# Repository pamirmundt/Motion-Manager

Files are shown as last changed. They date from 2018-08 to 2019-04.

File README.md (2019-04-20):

# Motion Manager (v1.0.0)
Controller for HNP Mikrosysteme micro annular gear pump MZR-7223
- 100 Hz PI RPM control with a RPM MAP filter
- 5 Hz screen refresh
- 31.250 Hz PWM frequency

## Future Improvements
- Spaghetti code
- SD card reader and LCD need different SPI busses. (because LCD SPI does not have a CS option where SPI messes)
- 24V converter for fixed input
- Converter efficiency and heat problems with linear regulators (Linear regulator must be replaced with a switching converter)
- Voltage protection
- SPI is not enough for LCD, additional data bus lines should be used for feedback from LCD

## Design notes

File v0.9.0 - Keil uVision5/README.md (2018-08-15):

# MotionManager v0.9.0

- [X] Keil uVision5 project files
- [X] RPM Control
- [X] Voltage Control

- [ ] SD card support
- [ ] Logo reveal
- [ ] Flow rate display

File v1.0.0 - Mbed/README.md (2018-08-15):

# MotionManager v1.0.0

- [X] Mbed project files
- [X] RPM Control
- [X] Voltage Control
- [X] SD card support
- [X] Logo reveal
- [X] Flow rate display

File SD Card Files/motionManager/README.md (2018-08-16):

# About
#### SD card provides configuration parameters to MotionManager.
#### MotionManager only reads SD card on boot, during logo reveal.
#### MotionManager should be turned off and on, if any changes are done on the SD card.
#### SD card folder hierarchy should be "SDcard:\motionManager\configFile.csv"
#### If no SD card is provided or there is a missing .csv file, MotionManager uses its build in default parameters.
#### All parameters are in floating points and the syntax is "10.0,20.0,30.0", with commas between parameters and without any spaces.

## PID.csv

### (Kp,Ki,Kd,integralMin,integralMax,alpha)
#### Kp: Proportional Coefficient
#### Ki: Integral Coefficient
#### Kd: Derivative Coefficient
#### integralMin: Integral Sum Minimum Threshold
#### integralMax: Integral Sum Maximum Threshold
#### alpha: Moving average filter alpha value, [ accumulator = (alpha * new_value) + (1.0 - alpha) * accumulator ]

##### More about PID: https://en.wikipedia.org/wiki/PID_controller
##### More about moving average filter: https://en.wikipedia.org/wiki/Moving_average

## RPM.csv

### (refRpmResolution, refRpmUpperThreshold)
#### refRpmResolution: Reference RPM Resolution
#### refRpmUpperThreshold: Maximum Selectable Reference RPM

## encoder.csv

### (encoderPulsePerRev)
#### encoderPulsePerRev: Encoder Resolution / Pulses Per Revolution

##### More about encoders: https://en.wikipedia.org/wiki/Rotary_encoder

## flowRateVersusVoltage.csv

### (A,B,C)
#### Quadratic function constants for Flow Rate(ml/min) versus voltage
#### Flow Rate = A * (Voltage)^2 + B * voltage + C

##### Quadratic curve fitting: https://www.wolframalpha.com/input/?i=quadratic+fit&lk=3

## voltage.csv

### (voltageResolution,voltageUpperThreshold)
#### voltageResolution: Selectable voltage resolution
#### voltageUpperThreshold: Maximum selectable voltage

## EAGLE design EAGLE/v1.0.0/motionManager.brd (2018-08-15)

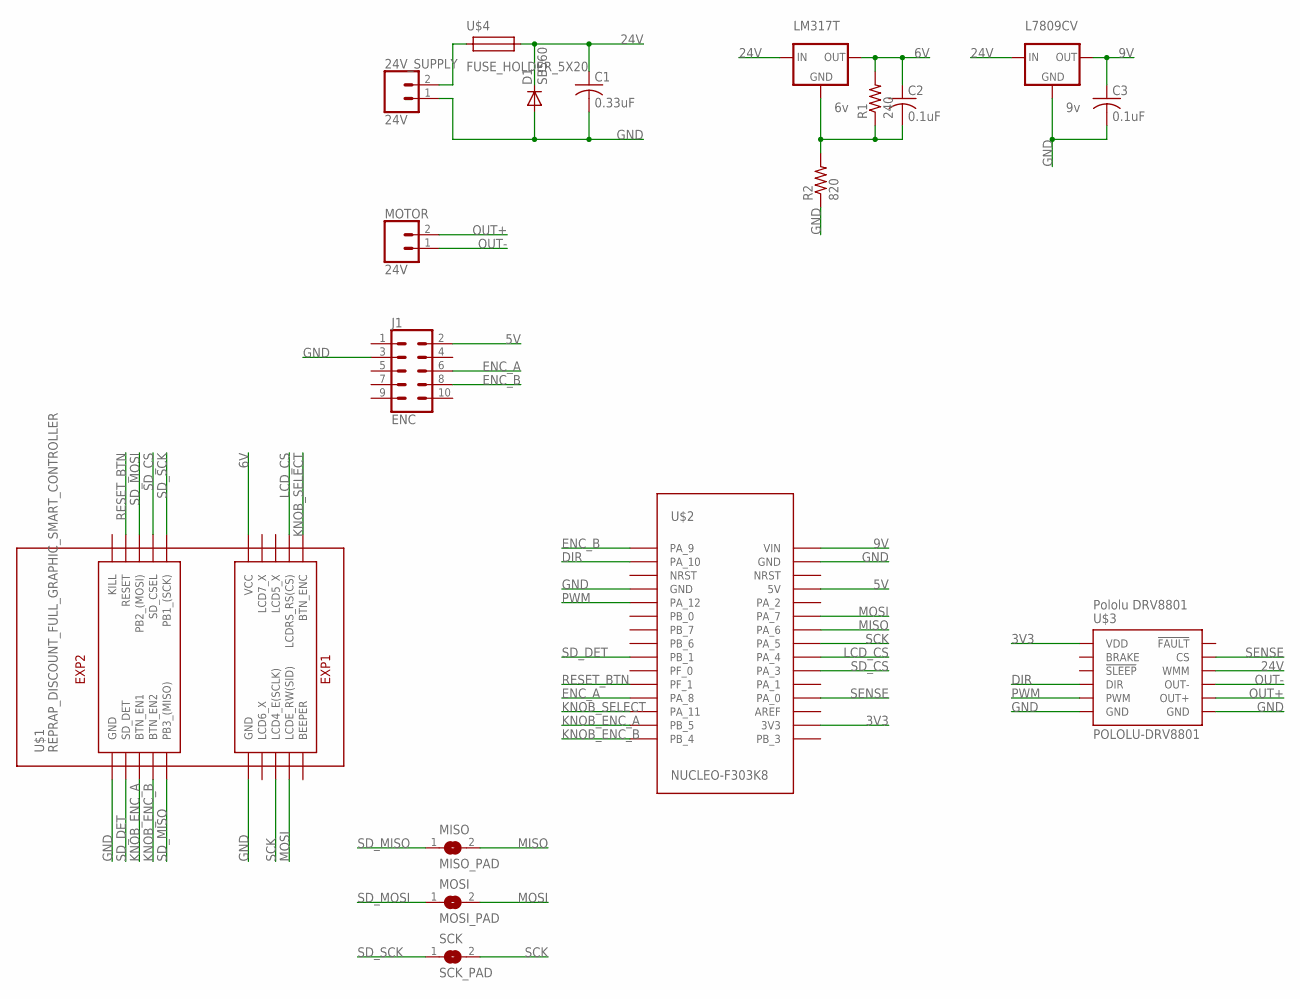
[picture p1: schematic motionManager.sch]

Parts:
24V_SUPPLY: 24V; SCREWTERMINAL-5MM-2
C1: 0.33uF; C025_050-055X075
C2, C3: 0.1uF; C025_050-055X075
D1: SB560; DO201-15
J1: ENC; 2X5-SHROUDED-NS
L7809CV: 9v; 78XXL
LM317T: 6v; 78XXL
MISO: MISO_PAD; SJW
MOSI: MOSI_PAD; SJW
MOTOR: 24V; SCREWTERMINAL-5MM-2
R1: 240; 0207/7
R2: 820; 0207/7
SCK: SCK_PAD; SJW
U$1: REPRAP_DISCOUNT_FULL_GRAPHIC_SMART_CONTROLLER
U$2: NUCLEO-F303K8
U$3: POLOLU-DRV8801
U$4: FUSE_HOLDER_5X20

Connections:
3V3: U$2.3V3, U$3.VDD
5V: J1.2, U$2.5V
6V: C2.1, LM317T.OUT, R1.2, U$1.VCC
9V: C3.1, L7809CV.OUT, U$2.VIN
24V: C1.1, D1.C, L7809CV.IN, LM317T.IN, U$3.VMM (WMM), U$4.P$2
DIR: U$2.PA_10, U$3.DIR
ENC_A: J1.6, U$2.PA_8
ENC_B: J1.8, U$2.PA_9
GND: 24V_SUPPLY.1, C1.2, C3.2, D1.A, J1.3, L7809CV.GND, R2.1, U$1.GND@0 (GND), U$1.GND@1 (GND), U$2.GND@0 (GND), U$2.GND@1 (GND), U$3.GND@1 (GND), U$3.GND@2 (GND)
KNOB_ENC_A: U$1.BTN_EN1, U$2.PB_5
KNOB_ENC_B: U$1.BTN_EN2, U$2.PB_4
KNOB_SELECT: U$1.BTN_ENC, U$2.PA_11
LCD_CS: U$1.LCDRS_RS(CS), U$2.PA_4
MISO: MISO.2, U$2.PA_6
MOSI: MOSI.2, U$1.LCDE_RW(SID), U$2.PA_7
unnamed: 24V_SUPPLY.2, U$4.P$1
unnamed: C2.2, LM317T.GND, R1.1, R2.2
OUT+: MOTOR.2, U$3.OUT+
OUT-: MOTOR.1, U$3.OUT-
PWM: U$2.PA_12, U$3.PWM
RESET_BTN: U$1.RESET, U$2.PF_1
SCK: SCK.2, U$1.LCD4_E(SCLK), U$2.PA_5
SD_CS: U$1.SD_CSEL, U$2.PA_3
SD_DET: U$1.SD_DET, U$2.PB_1
SD_MISO: MISO.1, U$1.PB3_(MISO)
SD_MOSI: MOSI.1, U$1.PB2_(MOSI)
SD_SCK: SCK.1, U$1.PB1_(SCK)
SENSE: U$2.PA_0, U$3.CS

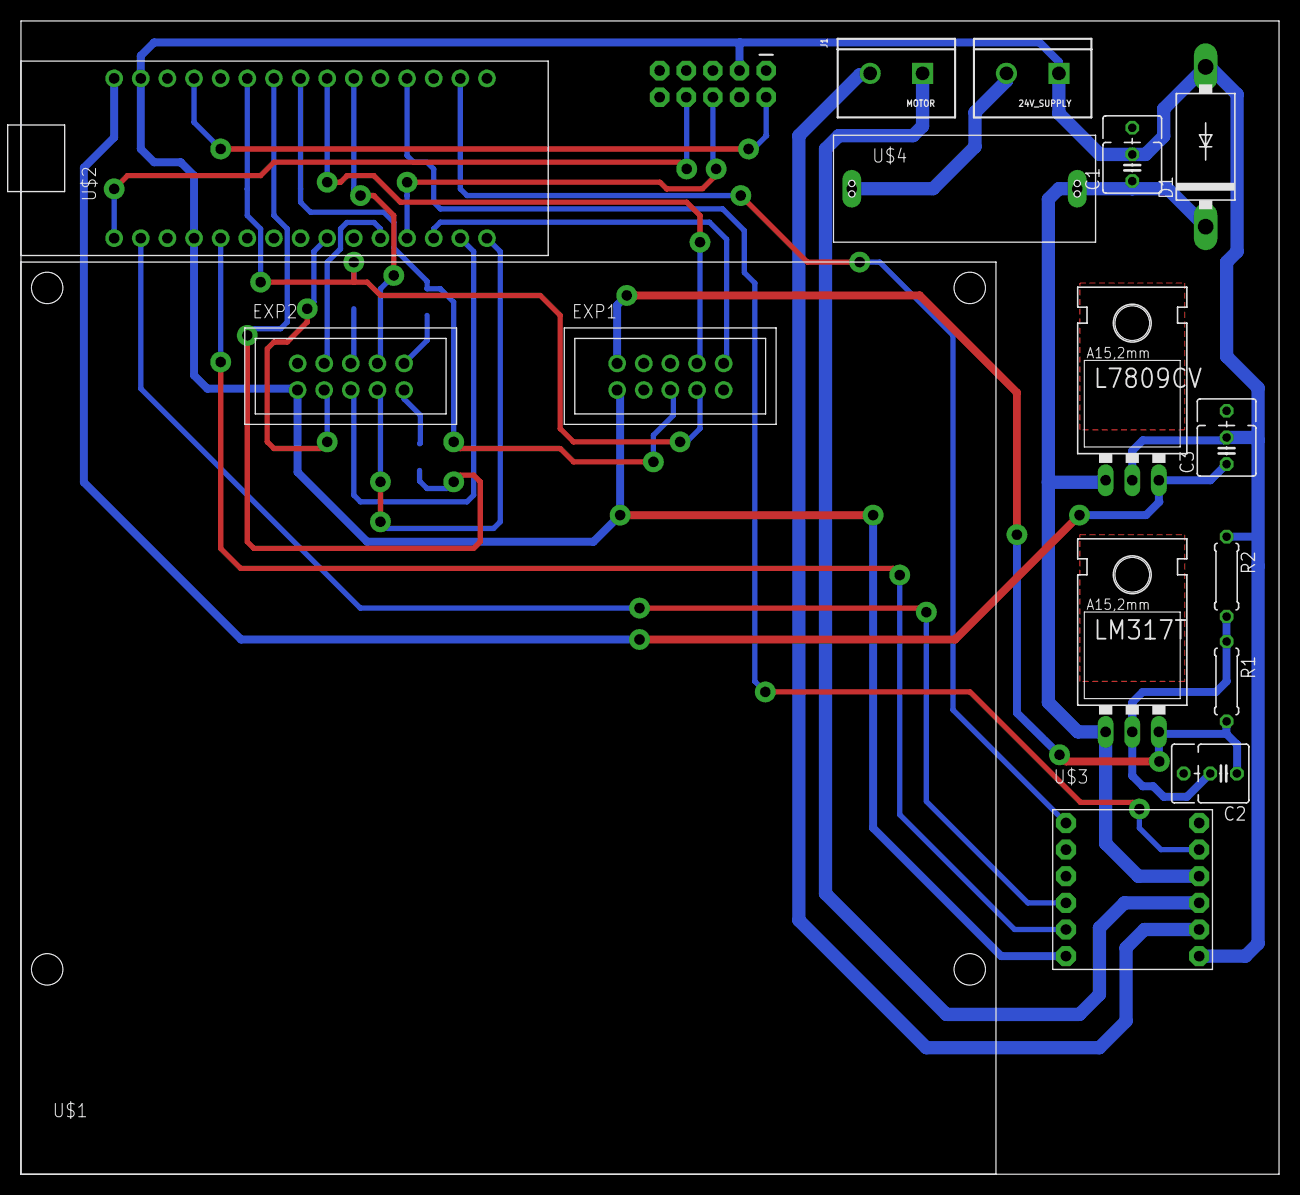
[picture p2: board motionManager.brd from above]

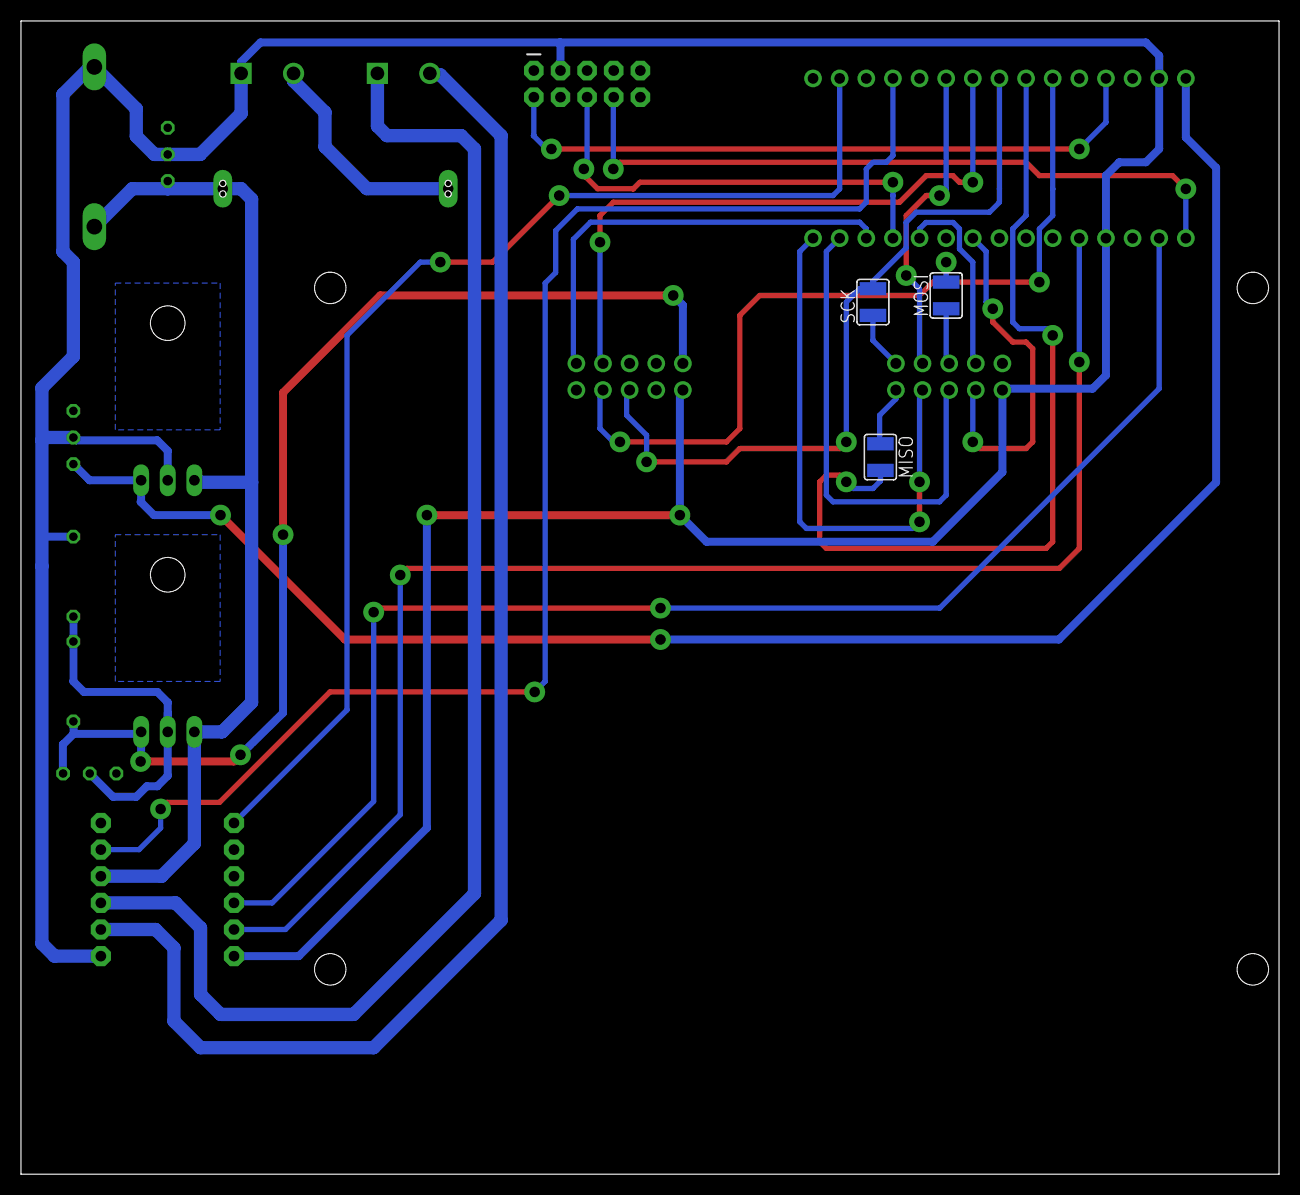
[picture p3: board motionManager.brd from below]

Board: 2 copper layers, 120.0 x 110.0 mm, 18 parts (3 on the bottom side), 28 nets.

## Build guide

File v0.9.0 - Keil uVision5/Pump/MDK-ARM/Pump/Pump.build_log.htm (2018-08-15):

µVision Build Log

Tool Versions:

IDE-Version: µVision V5.24.2.0
Copyright (C) 2017 ARM Ltd and ARM Germany GmbH. All rights reserved.
License Information: Pamir Mundt, Sabanci University, LIC=----
 
Tool Versions:
Toolchain:       MDK-Lite  Version: 5.24.1
Toolchain Path:  D:\Keil_v5\ARM\ARMCC\Bin
C Compiler:      Armcc.exe V5.06 update 5 (build 528)
Assembler:       Armasm.exe V5.06 update 5 (build 528)
Linker/Locator:  ArmLink.exe V5.06 update 5 (build 528)
Library Manager: ArmAr.exe V5.06 update 5 (build 528)
Hex Converter:   FromElf.exe V5.06 update 5 (build 528)
CPU DLL:         SARMCM3.DLL V5.24.1
Dialog DLL:      DCM.DLL V1.16.0.0
Target DLL:      STLink\ST-LINKIII-KEIL_SWO.dll V3.0.1.0
Dialog DLL:      TCM.DLL V1.32.0.0

Project:

C:\Users\Mundt\Desktop\Pump\MDK-ARM\Pump.uvprojx
Project File Date:  08/09/2018

Output:

*** Using Compiler 'V5.06 update 5 (build 528)', folder: 'D:\Keil_v5\ARM\ARMCC\Bin'
Build target 'Pump'
"Pump\Pump.axf" - 0 Error(s), 0 Warning(s).

Software Packages used:

Package Vendor: ARM
                http://www.keil.com/pack/ARM.CMSIS.5.3.0.pack
                ARM.CMSIS.5.3.0
                CMSIS (Cortex Microcontroller Software Interface Standard)
   * Component: CORE Version: 5.1.1

Package Vendor: Keil
                http://www.keil.com/pack/Keil.STM32F3xx_DFP.2.1.0.pack
                Keil.STM32F3xx_DFP.2.1.0
                STMicroelectronics STM32F3 Series Device Support and Examples

Collection of Component include folders:

  .\RTE\_Pump
  D:\Keil_v5\ARM\PACK\ARM\CMSIS\5.3.0\CMSIS\Include
  D:\Keil_v5\ARM\PACK\Keil\STM32F3xx_DFP\2.1.0\Drivers\CMSIS\Device\ST\STM32F3xx\Include

Collection of Component Files used:

   * Component: ARM::CMSIS:CORE:5.1.1
Build Time Elapsed:  00:00:01

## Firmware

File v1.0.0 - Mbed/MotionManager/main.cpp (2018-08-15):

#include "mbed.h"
#include "main.h"
#include "LCD.h"
#include "SDFileSystem.h"
#include "logo.h"

// DEBUG
//Serial pc(SERIAL_TX, SERIAL_RX);

/* Private variables ---------------------------------------------------------*/
SPI_HandleTypeDef hspi1;
TIM_HandleTypeDef htim1;
TIM_HandleTypeDef htim3;
TIM_HandleTypeDef htim15;
TIM_HandleTypeDef htim16;
TIM_HandleTypeDef htim17;

// mosi, miso, sclk, cs
SDFileSystem sd(PA_7, PA_6, PA_5, PA_3, "sd");

/* Private variables ---------------------------------------------------------*/
#define encodingType 4.0f //Quadrature Encoding
#define RPMCalculationFreq 100.0f

#define pwmResolution 2048

#define debounceMillis 400

LCD * lcd;

/*******************************************************************************
    RPM Resolution per encoder tick
        (Encoder tick/sec) to RPM

                        60sec * (Frequency of RPM calculation timer)
    RPM_res_per_tick = ----------------------------------------------
                        Encoder Resolution * Encoder Reading Mode(x4)
*******************************************************************************/
#define RPM_res_per_tick (60.0f * RPMCalculationFreq) / (encoderPulsePerRev * encodingType)

// RPM Calculation
volatile int16_t prevEncoderCount = 0;
volatile float motorRPM = 0.0f;

//Moving Average for RPM smoothing
volatile float averagedMotorRpm = 0.0f;
volatile float alpha = 0.128f;

// Voltage Control
volatile float voltage = 0.0f;

// PI Control
volatile float Kp = 0.02f;
volatile float Ki = 0.01f;
volatile float Kd = 0.0f;
volatile float integral = 0.0f;
volatile float integralMin = -2048.0f;
volatile float integralMax = 2048.0f;

volatile float refRpm = 0.0f;

// Encoder
float encoderPulsePerRev = 100.0f;

// Voltage
float voltageLowerThreshold = 0.0f;
float voltageUpperThreshold = 24.0f;
float voltageResolution = 0.1f;

// RPM
float refRpmLowerThreshold = 0.0f;
float refRpmUpperThreshold = 10000.0f;
float refRpmResolution = 100.0f;

//Flow Rate
//volatile float flowRate = 0.0f;
// Flow Rate versus Voltage
// Quadratic Function Parameters
// FR = f(V) = A*V^2 + B*V + C
float A = 0.0f, B = 0.0f, C = 0.0f;

//Display Selection
volatile float displayedRefRpm = 0.0f;
volatile float displayedVoltage = 0.0f;

// Rotary Knob
volatile uint8_t prevState = 0;
volatile int16_t cycleCount = 0;

//Debouncing
uint32_t currentMillis = 0;
uint32_t prevMillis = 0;

int pwm = 0;

const int cw[4] = {
              2, // 10 -> 11
              0, // 00 -> 10
              3, // 11 -> 01
              1  // 01 -> 00
            };

const int ccw[4] = {
              1, // 01 -> 11
              3, // 11 -> 10
              0, // 00 -> 01
              2  // 10 -> 00
            };

            
// Screen Menu Button Track - Select and Deselect
uint8_t selected = false;

// Underline of "Ref RPM"
uint8_t underlineHighlighted = false;
            
// Menu
enum menu{
    Logo,
    ControlSelection,
    RpmControl,
    VoltageControl,
    About
};

/* Private function prototypes -----------------------------------------------*/
void SystemClock_Config(void);
static void MX_GPIO_Init(void);
static void MX_TIM1_Init(void);
static void MX_TIM16_Init(void);
static void MX_TIM3_Init(void);
static void MX_SPI1_Init(void);
static void MX_TIM17_Init(void);
static void MX_TIM15_Init(void);

void HAL_TIM_MspPostInit(TIM_HandleTypeDef *htim);

enum menu menuSelection = Logo;

void applyPWM(int16_t pwmValue){
    //Forward
    if(pwmValue > 0){
        if(pwmValue > pwmResolution){
            pwmValue = pwmResolution;
            pwm = pwmValue;
        }
        HAL_GPIO_WritePin(GPIOA, GPIO_PIN_10, GPIO_PIN_RESET);
    }
    //Backward
    else{
        if(pwmValue < -pwmResolution){
            pwmValue = -pwmResolution;
            pwm = pwmValue;
        }
        HAL_GPIO_WritePin(GPIOA, GPIO_PIN_10, GPIO_PIN_SET);
    }
    pwmValue = abs(pwmValue);
    pwm = pwmValue;
    __HAL_TIM_SET_COMPARE(&htim16, TIM_CHANNEL_1, pwmValue);
}

// Increase Displayed Reference RPM
void incrementDisplayedRefRPM(void){
    if(displayedRefRpm < refRpmUpperThreshold)
        displayedRefRpm += refRpmResolution;
}

// Decrease Displayed Reference RPM
void decreaseDisplayedRefRPM(void){
    if(refRpmLowerThreshold < displayedRefRpm)
        displayedRefRpm -= refRpmResolution;
}

// Increase Displayed Voltage
void incrementDisplayedVoltage(void){
    if(displayedVoltage < voltageUpperThreshold)
        displayedVoltage += voltageResolution;
}

// Decrease Displayed Voltage
void decreaseDisplayedVoltage(void){
    if(voltageLowerThreshold < displayedVoltage)
        displayedVoltage -= voltageResolution;
}

//Count the Digits before .
uint8_t digitsInFloat(unsigned char * f){
    uint8_t i = 0;
    uint8_t digitCount = 0;
    while(f[i++] != '.'){
        digitCount++;
    }
    return digitCount;
}

//Calculate Flow Rate from Voltage - Quadratic Function
float calculateFlowRate(float _volt){
    float flowRate = (A * _volt * _volt) + (B * _volt) + C;
    return flowRate;
}

//Refresh Numbers on the screen
void refreshScreen(void){
    //Clear Second Row - Fill with Spaces
    DisplayStringLeftAlligned(lcd,1,0, (unsigned char *)"                ", strlen("                "));
    //Clear Fourth Rows First Half - Fill with Spaces
    DisplayStringLeftAlligned(lcd,3,0, (unsigned char *)"        ", strlen("        "));

    unsigned char * array = (unsigned char *)malloc(16);
    
    if(menuSelection == RpmControl){
        if(selected == true)
            sprintf((char *)array, "%.1f", displayedRefRpm);
        else if(selected == false)
            sprintf((char *)array, "%.1f", refRpm);
    }
    else if(menuSelection == VoltageControl){
        if(selected == true){
            sprintf((char *)array, "%.1f", displayedVoltage);
        }
        else if(selected == false){
            sprintf((char *)array, "%.1f", voltage);
        }
    }
    
    uint8_t digitCount = digitsInFloat(array);

    // Display Reference RPM
    DisplayStringRightAlligned(lcd,1,6, array, digitsInFloat(array)+2);
    
    free(array);

    // RPM
    unsigned char * rpmStr = (unsigned char *)malloc(16); //16 digits max
    sprintf((char *)rpmStr, "%.1f", averagedMotorRpm);
    DisplayStringRightAlligned(lcd,1,15, rpmStr, digitsInFloat(rpmStr)+2);
    free(rpmStr);
    
    //Calculate Flow Rate
    float flowRate =0.0f;
    if(menuSelection == RpmControl)
        flowRate = calculateFlowRate(((float)pwm / ((float)pwmResolution)) * voltageUpperThreshold);
    else if(menuSelection == VoltageControl)
        flowRate = calculateFlowRate(voltage);
        
    // Flow Rate
    unsigned char * flowRateStr = (unsigned char *)malloc(16);
    sprintf((char *)flowRateStr, "%.1f", flowRate);
    DisplayStringRightAlligned(lcd,3,7, flowRateStr, digitsInFloat(flowRateStr)+2);
    free(flowRateStr);
}

// Display underline of Ref RPM
void underlineHighlight(void){
    WriteInstruction(lcd, SET_GRAPHIC_RAM_ADDRESS | 29);
    WriteInstruction(lcd, 0x80);
    WriteRam(lcd, 0x7F);
    WriteRam(lcd, 0xFF);
    WriteRam(lcd, 0xFF);
    WriteRam(lcd, 0xFF);
    WriteRam(lcd, 0xFF);
    WriteRam(lcd, 0xFF);
    WriteRam(lcd, 0xFF);
}

// Hide underline of Ref RPM
void underlineLowlight(void){
    WriteInstruction(lcd, SET_GRAPHIC_RAM_ADDRESS | 29);
    WriteInstruction(lcd, 0x80);
    WriteRam(lcd, 0x00);
    WriteRam(lcd, 0x00);
    WriteRam(lcd, 0x00);
    WriteRam(lcd, 0x00);
    WriteRam(lcd, 0x00);
    WriteRam(lcd, 0x00);
    WriteRam(lcd, 0x00);
}

// Display Logo

// Display ControlSelection
uint8_t menuIndex = 0;

void menuControlSelection(void){
    menuSelection = ControlSelection;
    
    SetTextMode(lcd);
    ClearScreen(lcd);
    
    SetGraphicsMode(lcd);
    ClearGDRAM(lcd);
    
    for(uint8_t y = 0; y < 15; y++){
        for (uint8_t x = 0; x < 8; x++) {
            WriteInstruction(lcd, SET_GRAPHIC_RAM_ADDRESS | y);
            WriteInstruction(lcd, 0x80 | x);
            WriteRam(lcd, 0xFF);
            WriteRam(lcd, 0xFF);
        }
    }
        
    menuIndex = 1;
    HighlightMenuItem(lcd,menuIndex,true);
        
    SetTextMode(lcd);
    //ClearScreen(lcd);
    
    DisplayStringLeftAlligned(lcd,0,1, (unsigned char *)"MOTION MANAGER", strlen("MOTION MANAGER"));
    DisplayStringLeftAlligned(lcd,1,1, (unsigned char *)"RPM Control", strlen("RPM Control"));
    DisplayStringLeftAlligned(lcd,2,1, (unsigned char *)"Voltage Control", strlen("Voltage Control"));
    DisplayStringLeftAlligned(lcd,3,1, (unsigned char *)"About", strlen("About"));
}

void menuRpmControl(void){
    SetTextMode(lcd);
    ClearScreen(lcd);
    
    //TIM1 - Encoder
    HAL_TIM_Encoder_Start(&htim1, TIM_CHANNEL_ALL);
    
    //TIM3 - Velocity Calculation Interrupt
    HAL_TIM_Base_Start_IT(&htim3);
    
    //TIM16 - PWM
    HAL_TIM_PWM_Start(&htim16, TIM_CHANNEL_1);
    
    // Topic Background
    SetGraphicsMode(lcd);
    ClearGDRAM(lcd);
    
    DivideHalfInverseT(lcd);
    HighlightTopLeftText(lcd);
    HighlightTopRightText(lcd);
    HighlightBottomText(lcd);
    
    // Topics
    SetTextMode(lcd);
    
    DisplayStringLeftAlligned(lcd,0,0, (unsigned char *)"Ref RPM", strlen("Ref RPM"));
    DisplayStringLeftAlligned(lcd,0,9, (unsigned char *)"RPM", strlen("RPM"));
    DisplayStringLeftAlligned(lcd,2,0, (unsigned char *)"Flow Rate", strlen("Flow Rate"));
    DisplayStringRightAlligned(lcd,3,14, (unsigned char *)"ml/min", strlen("ml/min"));
    
    //TIM17 - Screen Refresh Rate - 64Mhz / 64000 / 99 = 10Hz
    HAL_TIM_Base_Start_IT(&htim17);
}

void menuVoltageControl(void){
    SetTextMode(lcd);
    ClearScreen(lcd);
    
    //TIM1 - Encoder
    HAL_TIM_Encoder_Start(&htim1, TIM_CHANNEL_ALL);
    
    //TIM3 - Velocity Calculation Interrupt
    HAL_TIM_Base_Start_IT(&htim3);
    
    //TIM16 - PWM
    HAL_TIM_PWM_Start(&htim16, TIM_CHANNEL_1);
    
    // Topic Background
    SetGraphicsMode(lcd);
    ClearGDRAM(lcd);
    
    DivideHalfInverseT(lcd);
    HighlightTopLeftText(lcd);
    HighlightTopRightText(lcd);
    HighlightBottomText(lcd);
    
    // Topics
    SetTextMode(lcd);
    
    DisplayStringLeftAlligned(lcd,0,0, (unsigned char *)"Voltage", strlen("Voltage"));
    DisplayStringLeftAlligned(lcd,0,9, (unsigned char *)"RPM", strlen("RPM"));
    DisplayStringLeftAlligned(lcd,2,0, (unsigned char *)"Flow Rate", strlen("Flow Rate"));
    DisplayStringRightAlligned(lcd,3,14, (unsigned char *)"ml/min", strlen("ml/min"));
    
    //TIM17 - Screen Refresh Rate - 64Mhz / 64000 / 99 = 10Hz
    HAL_TIM_Base_Start_IT(&htim17);
}

void menuAbout(){
    SetTextMode(lcd);
    ClearScreen(lcd);
    
    SetGraphicsMode(lcd);
    ClearGDRAM(lcd);
    
    SetTextMode(lcd);
    DisplayStringLeftAlligned(lcd,0,0, (unsigned char *)"info@", strlen("info@"));
    DisplayStringLeftAlligned(lcd,1,0, (unsigned char *)"kopernikrobotics", strlen("KopernikRobotics"));
    DisplayStringRightAlligned(lcd,2,15, (unsigned char *)".com", strlen(".com"));
    DisplayStringLeftAlligned(lcd,3,0, (unsigned char *)"v1.0.0", strlen("v1.0.0"));
}

void setVoltage(){
    pwm = (((float)voltage)/((float)voltageUpperThreshold)) * ((float)pwmResolution);
    __HAL_TIM_SET_COMPARE(&htim16, TIM_CHANNEL_1, (int)pwm);
}

/* MAIN ***********************************************************************/
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

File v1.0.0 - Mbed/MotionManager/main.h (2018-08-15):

/**
  ******************************************************************************
  * @file           : main.h
  * @brief          : Header for main.c file.
  *                   This file contains the common defines of the application.
  ******************************************************************************
  ** This notice applies to any and all portions of this file
  * that are not between comment pairs USER CODE BEGIN and
  * USER CODE END. Other portions of this file, whether 
  * inserted by the user or by software development tools
  * are owned by their respective copyright owners.
  *
  * COPYRIGHT(c) 2018 STMicroelectronics
  *
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
  ******************************************************************************
  */

/* Define to prevent recursive inclusion -------------------------------------*/
#ifndef __MAIN_H__
#define __MAIN_H__

/* Includes ------------------------------------------------------------------*/

/* USER CODE BEGIN Includes */

/* USER CODE END Includes */

/* Private define ------------------------------------------------------------*/

#define MCO_Pin GPIO_PIN_0
#define MCO_GPIO_Port GPIOF
#define VCP_TX_Pin GPIO_PIN_2
#define VCP_TX_GPIO_Port GPIOA
#define RS_Pin GPIO_PIN_4
#define RS_GPIO_Port GPIOA
#define DIR_Pin GPIO_PIN_10
#define DIR_GPIO_Port GPIOA
#define SWDIO_Pin GPIO_PIN_13
#define SWDIO_GPIO_Port GPIOA
#define SWCLK_Pin GPIO_PIN_14
#define SWCLK_GPIO_Port GPIOA
#define VCP_RX_Pin GPIO_PIN_15
#define VCP_RX_GPIO_Port GPIOA

/* ########################## Assert Selection ############################## */
/**
  * @brief Uncomment the line below to expanse the "assert_param" macro in the 
  *        HAL drivers code
  */
/* #define USE_FULL_ASSERT    1U */

/* USER CODE BEGIN Private defines */

/* USER CODE END Private defines */

#ifdef __cplusplus
 extern "C" {
#endif
void _Error_Handler(char *, int);

#define Error_Handler() _Error_Handler(__FILE__, __LINE__)
#ifdef __cplusplus
}
#endif

#endif /* __MAIN_H__ */

/************************ (C) COPYRIGHT STMicroelectronics *****END OF FILE****/

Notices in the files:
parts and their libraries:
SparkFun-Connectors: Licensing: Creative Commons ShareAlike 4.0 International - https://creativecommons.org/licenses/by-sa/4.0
